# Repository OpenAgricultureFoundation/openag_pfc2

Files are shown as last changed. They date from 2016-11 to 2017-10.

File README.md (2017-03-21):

# openag_pfc2
This repository contains many resources for constructing a Personal Food Computer v2 (beta)

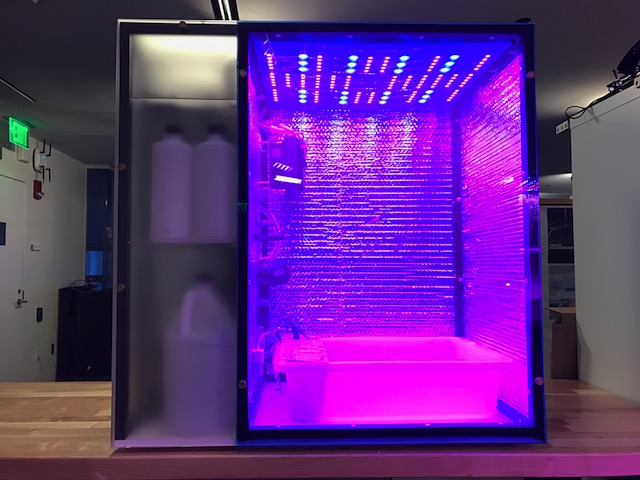
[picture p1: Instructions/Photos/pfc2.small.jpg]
pfc2


## Build Instructions

For many more photos and step by step build instructions, check out
[instructions.md](instructions.md).

## List of Resources

Resources included in this repository:
 - [Instructions](instructions.md): How to build a PFC2
 - [Build Video](https://youtu.be/Uf1FqjcPWsI): Video Walkthrough on the build. Good visual cues.
 - [Master Bill of Materials](BOM/BOM_MASTER.xlsx): Tabbed spreadsheet of components needed to
   build the PFC2
    - Ordering BOM: Components you will need to order from suppliers
    - Kit BOM: Components included in the PFC2 kit **\[NOTE: The kits are not available yet\]**
    - WIR-HAR-PCK-\*: Wiring harness component pack details
    - __FAS-PCK-0001: Fastener component pack details__ (The sheet with baggie number information on it)
    - STR-FOM-PCK-0001: Sealing foam component pack details
    - STR-PNL-PCK-\*: Panel and sticker component pack details
    - STR-BAR-PCK-0001: Bar component pack details
    - Raw Materials: Stock materials including aluminum bar, acrylic and HDPE panels,
      insulation, foam, etc. that can be used to make many of the components in the
      STR-BAR-\*, STR-PNL-\*, STR-FOM-\*, and STR-INS-\* component packs
 - [Sub Assembly Bill of Materials](BOM/BOM_Sub_Assemblys.xlsx): Tabbed spreadsheet of
   details on the sub assembly components
    - Temperature Control Assembly: Heating element, fan, and PC water cooling radiator
    - Chiller Assembly: Fan, mounting plate, and PC water cooling chiller
    - Peristaltic Pumps: Nutrient and pH solution pumps and pump mounting panel
    - Power Module: Power entry module, power switch, and DC power supplies
    - Light Manifold: LEDs, camera, and mounting panel
    - Water Manifold: Sensors, panels, pump, filter, etc.
    - Brain Manifold: Signal board, Raspberry Pi Model 3, Arduino Mega, etc.
 - [Solidworks CAD Model](CAD/GrabCAD/OpenAG-Personal-Food-Computer-V2): Comprehensive view of where
   parts belong in the computer
 - [Drawings](CAD/GrabCAD/Drawings): Documentation for machining parts or
   sending to a contract machinist
 - [DXF Files](CAD/GrabCAD/DXF): File format used for laser cutting parts
 - [Wire Harnesses](Wire_Harnesses.xlsx): Bill of Materials and instructions for creating
   the wire harnesses
 - [Wiring Reference](Wiring_Reference.xlsx): Reference when wiring up the device
 - [Connectorization](Connectorization.xlsx): Bill of Materials and instructions for
   attaching connectors to the chiller, fans, pumps, LEDs, etc.

### Tools
For 3D model Access, Go to [http://www.edrawingsviewer.com/](http://www.edrawingsviewer.com/) for a free & legitmate CAD document viewing software.

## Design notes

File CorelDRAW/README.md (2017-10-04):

# CorelDRAW files
These files were made by importing the .DXF files into CorelDRAW.
They are used on the Spirit laser cutter in the MIT ML Fab shop.

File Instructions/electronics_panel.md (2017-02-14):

## Assemble The Electronics Panel Components

#### Tools
- 1/16" Hex Driver
- 3/32" Hex Driver
- 1/4" Nut Driver
- 1/4" wrench

### Wire Seals
1. Gather foam squares **STR-FOM-0001**, **STR-FOM-0002**, & acrylic square **STR-PNL-0010**  from the foam pack.
2. Remove the adhesive protection from the foam
3. Match the patterns of the foam to their respective spots, and stick on.  **STR-FOM-0002** sticks to the electronics panel **STR-PNL-0017**, **STR-FOM-0001** sticks to the **STR-PNL-0010** backing plate.
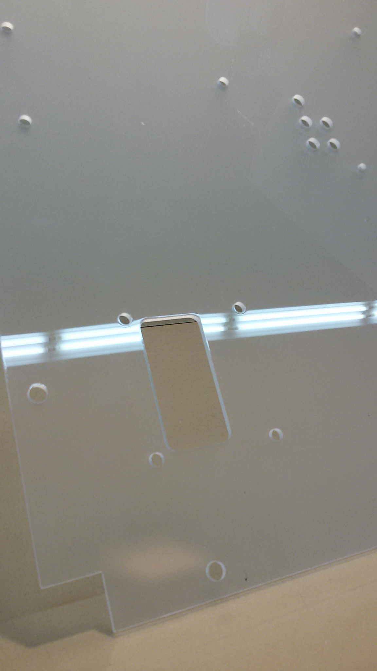
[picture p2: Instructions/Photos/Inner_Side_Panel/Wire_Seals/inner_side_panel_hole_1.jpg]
inner side panel hole

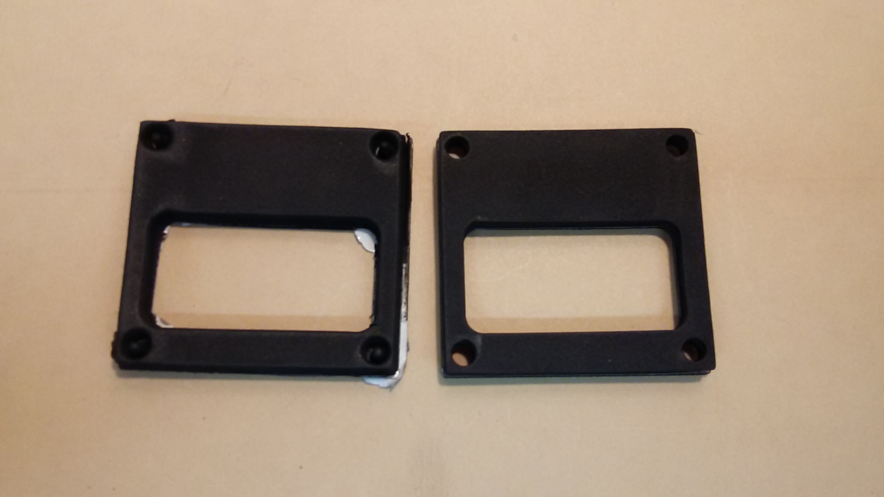
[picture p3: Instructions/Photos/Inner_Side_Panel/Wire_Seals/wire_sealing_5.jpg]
foam

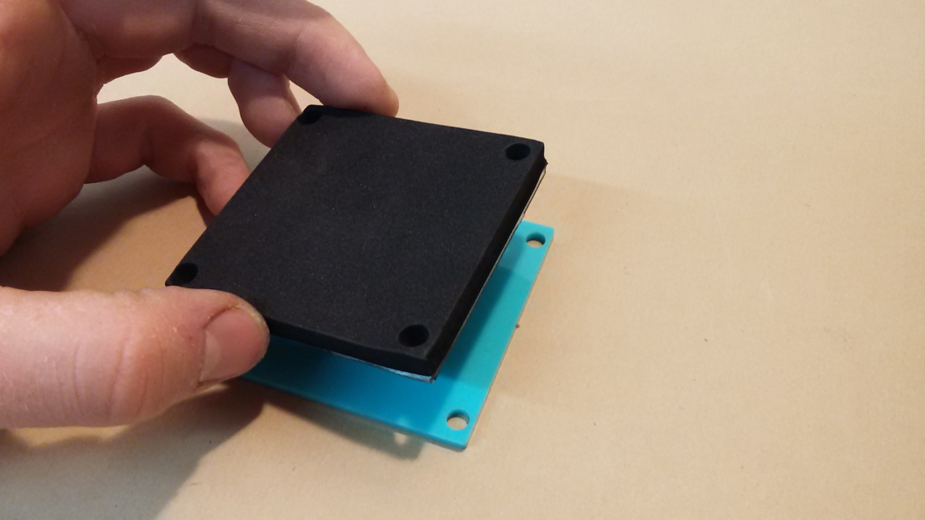
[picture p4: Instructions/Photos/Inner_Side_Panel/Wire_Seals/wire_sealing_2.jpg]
backing plate


4. Note the orientation arrow on the acrylic plate. This indicates the direction the wires should pass through to seal.

### Pump Assembly
1. Collect components listed in **Sub Assembly BOM's** **Peristaltic Pumps** tab.
2. Locate orientation arrow. The pumps mount relative to this.
3. Slot the pump through the hole, with attention to the direction its wires point.
4. All pumps wires should face to the right relative to the arrow. The tubes should face outward.
  * if the wires face the wrong direction, the body can be easily uncliped & rotated 90^o
5. Tighten each pump on using x2 **S-#04-40-375-BTN-S-SS (Bag 14)** (4-40 x 0375 button head) and **S-#04-40-094-NUT-H-SS (Bag 15)** (#4-40 nut)
6. Mount x4 **S-#08-32-250-STD-H-AL-FF (Bag 9)**(8-32x2.5 female alum standoff) in the remaining holes using **S-#08-32-375-BTN-S-SS (Bag 2)**(8-32x0375 button head)
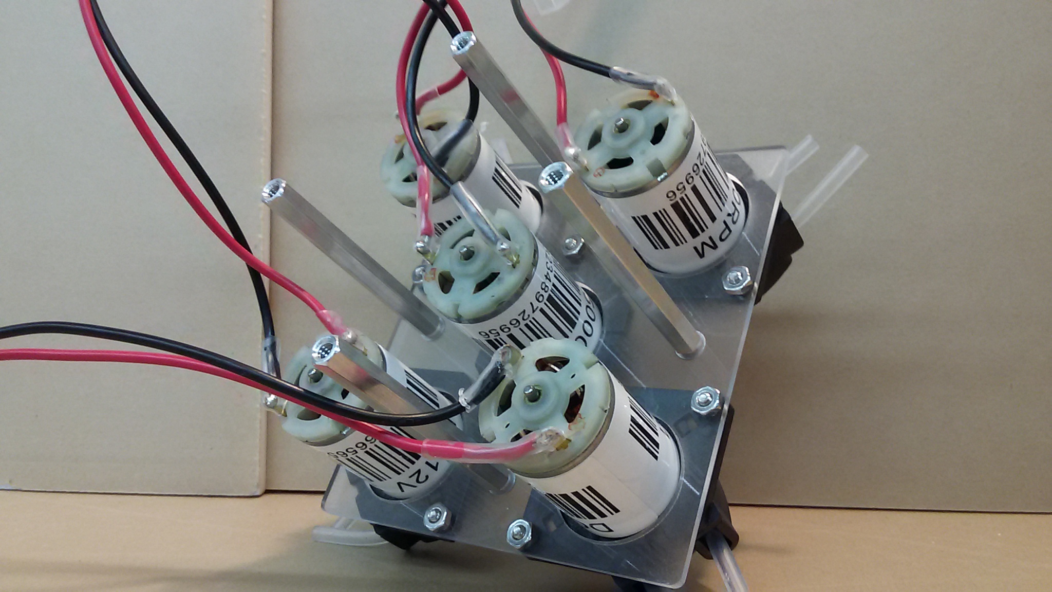
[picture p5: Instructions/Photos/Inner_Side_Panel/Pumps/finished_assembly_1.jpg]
Peristaltic Pumps Finished Assembly


### Side Camera
1. Stick adhesive backed **STR-FOM-0003 (Foam for camera sealing)** to the the camera **SEN-PRB-0005** board as shown.
2. Place the camera **SEN-PRB-0005** in its port on the inner side panel **STR-PNL-0017**, securing inplace with x4 **S-#02-56-375-BTN-S-SS (Bag 22)** & **S-#02-56-063-NUT-H-SS (Bag 23)**.  Note the orientationof the camera.
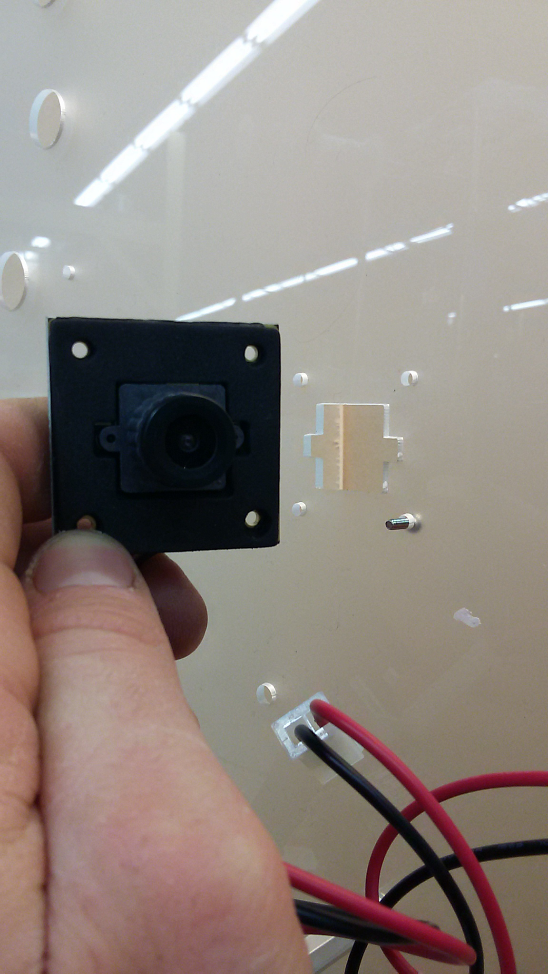
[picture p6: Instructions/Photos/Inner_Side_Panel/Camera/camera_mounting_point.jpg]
Camera with foam, at mounting point


### Humidity sensor
1. Place the Mount for the Humidity/temp sensor **SEN-MNT-0001** over its port. Secure inplace using x2 **S-#04-40-050-BTN-S-SS (Bag 11)** & **S-#04-40-094-NUT-H-SS (Bag 15)**.
2. Place the humidity sensor **SEN-PRB-CZD-0002** in at any time, tightening the screw on the side to secure the sensor.

### CO2 Sensor
1. Remove the CO2 sensor **SEN-PRB-CZD-0001** from its package, and put the small wire harness with black connectors to the side. This is not used.
2. Connect the harness with white connectors from the sensor to the blue board.
3. Push the sensor throught the port beneath the humidity/temp sensor port.
4. The small blue board can be neatly taped to the top of the sensor.
5. After full model assembly is complete, seal around its diameter with silicone sealant.
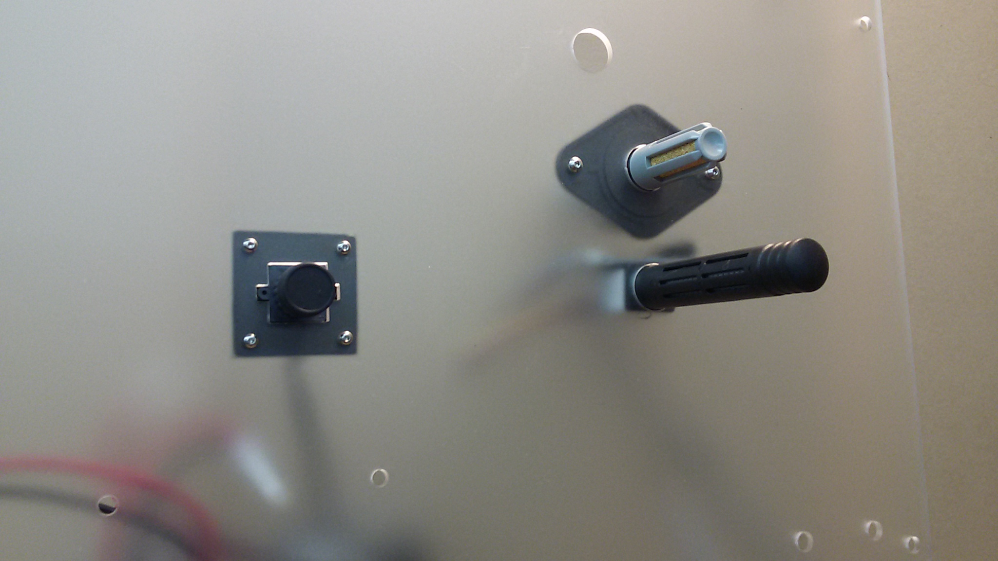
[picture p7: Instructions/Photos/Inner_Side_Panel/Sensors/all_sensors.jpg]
Picture of all sensors


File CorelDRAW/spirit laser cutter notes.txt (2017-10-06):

When corel prompts you to login, just hit "Skip" in the lower left.

Print > properties > paper tab - 960mm x 610mm   use this for page size.
You MUST check the Extend box.

When printing, use hairline pen type.  Select all, show object properties menu, select pen type hairline.

print then properties page for black color:
speed: 1.0
power: 100%
PPI: 1500
Air: on

For blue (if anything needs to be etched in the surface):
speed: 50.
power: 15%
PPI: default (400)
Air: on

You may need to print it a second time if it doesn't cut all the way through.

Anything you want etched, make blue then use lower power / higher speed.

Files:
- EB-panel-side is the left side cover for the electronics and side of fluid bay.
- EB-panel-front is the front fluid bay cover.
- door is the entrance to the growth chamber.

When using file "door with PFC etch", the black pen will do the lasing.  Set to 50/50/400

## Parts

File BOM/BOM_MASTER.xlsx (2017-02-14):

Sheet: Ordering BOM
Qty | Part Number | Description | Link | Distributor | Distributor Part Number
1 | STR-RAW-0010 | FOAM PLANT RAFT | https://www.amazon.com/Beaver-Plastics-Lettuce-Raft-72/dp/B01GG96JSA | Amazon
1 | ACT-CIR-0001 | NE555 Pulse Generator Adjustable Frequency Module 5-12V DC | https://www.amazon.com/gp/product/B00LHBZCCC/ref=oh_aui_search_detailpage?ie=UTF8&psc=1 | Amazon
1 | ACT-COV-0001 | 120mm Fan Guard | https://www.amazon.com/Metal-Finger-Guard-Computer-Cooling/dp/B00Y20QI0K | Amazon
1 | ACT-FLT-0001 | 1/2" Twist-On Pipe Strainer filter | https://www.amazon.com/gp/product/B000V2W0GE/ref=oh_aui_detailpage_o04_s00?ie=UTF8&psc=1 | Amazon
6 | ACT-FTG-0001 | G1/4" to 0375" Barb Fitting Black Chrome | https://www.amazon.com/s?url=search-alias%3Dcomputers&field-keywords=g1%2F4+to+3%2F8 | Amazon
1 | ACT-MIS-0001 | ASCS Small Active Aqua Air Stone Cylinder | https://www.amazon.com/gp/product/B00564Q784/ref=oh_aui_detailpage_o08_s00?ie=UTF8&psc=1 | Amazon
1 | ACT-PMP-0001 | Submersible Water Circulation Pump, 2.1 GPM | https://www.amazon.com/gp/product/B0196WL55G/ref=oh_aui_detailpage_o04_s00?ie=UTF8&psc=1 | Amazon
5 | ACT-PMP-0002 | Peristaltic Pump | https://www.amazon.com/Homecube-Peristaltic-Miniature-Aquarium-Analytical/dp/B0196LDFJQ | Amazon
1 | ACT-PMP-0003 | XSPC Ion Pump/reservoir combo | https://www.amazon.com/gp/product/B01BA3LY64/ref=oh_aui_detailpage_o04_s01?ie=UTF8&psc=1 | Amazon
1 | ACT-PMP-0004 | Mini Air Pump 12v Kpm27h Keurig Coffee Air Purge Pump | https://www.amazon.com/gp/product/B00ECCPT80/ref=oh_aui_detailpage_o01_s02?ie=UTF8&psc=1 | Amazon
40 | ACT-TBG-0001 | ATP Vinyl-Flex PVC Food Grade Plastic Tubing, Clear, 1/8" ID x 1/4" OD (By the Foot) | https://www.amazon.com/gp/product/B00E6BCV0G/ref=ox_sc_act_title_3?ie=UTF8&psc=1&smid=ATVPDKIKX0DER | Amazon
5 | ACT-TBG-0002 | PrimoFlex Advanced LRT 0375in.ID x 5/8in.OD Tubing Bundle (By the Foot) | https://www.amazon.com/gp/product/B00A0Q55MC/ref=ox_sc_act_title_2?ie=UTF8&psc=1&smid=A15YNZR7YB053N | Amazon
15 | ACT-TBG-0003 | Standard Airline Tubing (By the Inch) | https://www.amazon.com/gp/product/B0002APXOQ/ref=oh_aui_detailpage_o01_s01?ie=UTF8&psc=1 | Amazon
2 | ACT-VLV-0001 | 1/2" DC12V SS304 Motorized Valve,Electrical Ball Valve CR-02 | https://www.amazon.com/dp/B00OUTP6D8 | Amazon
1 | ACT-XNG-0001 | EX120 Single Fan Radiator | https://www.amazon.com/gp/product/B0067LW8HY/ref=oh_aui_detailpage_o00_s00?ie=UTF8&psc=1 | Amazon
1 | CSB-LIQ-0001 | General Hydroponics pH Up Liquid Fertilizer, 1-Quart | https://www.amazon.com/General-Hydroponics-Liquid-Fertilizer-1-Quart/dp/B005H78ZLC | Amazon
1 | CSB-LIQ-0002 | General Hydroponics pH Down Liquid Fertilizer, 1-Quart | https://www.amazon.com/General-Hydroponics-Liquid-Fertilizer-1-Quart/dp/B00CJID1I4 | Amazon
1 | CSB-LIQ-0003 | General Hydroponics FloraDuo A Mineral Nutrient, 1 Quart | https://www.amazon.com/General-Hydroponics-FloraDuo-Mineral-Nutrient/dp/B004PPY750 | Amazon
1 | CSB-LIQ-0004 | General Hydroponics FloraDuo B Mineral Nutrient, 1 Quart | https://www.amazon.com/General-Hydroponics-FloraDuo-Mineral-Nutrient/dp/B004IAB2F0 | Amazon
1 | CSB-MED-0001 | Oasis Horticubes (By the Tray of 104 Horticubes) | https://www.amazon.com/Oasis-Horticubes-2-Pack/dp/B007QVA7BS | Amazon
1 | ELC-MEM-0001 | SanDisk Ultra 32 GB Micro SDHC UHS-I | https://www.amazon.com/SanDisk-microSDHC-Standard-Packaging-SDSQUNC-032G-GN6MA/dp/B010Q57T02?s=pc | Amazon
1 | ELC-PRC-0001 | Arduino Mega 2560 w/USB A-to-B Cable | https://www.amazon.com/OSOYOO-MEGA2560-Control-ATMEGA2560-16AU-Compatible/dp/B00PD92EJ8?s=pc | Amazon
1 | ELC-PRC-0002 | Raspberry Pi 3 Model B | https://www.amazon.com/Raspberry-Pi-RASP-PI-3-Model-Motherboard/dp/B01CD5VC92?s=pc | Amazon
1 | ELC-REL-0001 | 16-Channel Relay Board | https://www.amazon.com/gp/product/B0057OC66U/ref=crt_ewc_title_dp_2?ie=UTF8&psc=1&smid=ATVPDKIKX0DER | Amazon
1 | ELC-REL-0002 | Multifunction Programmable Relay Timer | https://www.amazon.com/gp/product/B00VR1F3LC/ref=oh_aui_detailpage_o02_s02?ie=UTF8&psc=1 | Amazon
1 | FAS-MIS-0001 | 4" Mini Cable Ties, Black, (By the Pack of 100 Pieces) |  | Amazon
1 | PWR-REG-0001 | DC-DC Step-down Regulator 8-50V to 5V 3A with Micro USB Adapter Connector, Waterproof | https://www.amazon.com/gp/product/B00KKI4C1U/ref=ox_sc_act_title_4?ie=UTF8&psc=1&smid=AFHAE9RJVUMB | Amazon
1 | SEN-PRB-0003 | AM2315 Temperature & Humidity Sensor with Mount | https://www.amazon.com/gp/product/B011PR0WCW/ref=oh_aui_detailpage_o07_s01?ie=UTF8&psc=1 | Amazon
2 | SEN-PRB-0005 | ELP 2.1mm Wide Angle Mjpeg 5megapixel Hd Camera USB for Industrial,camera Module Usb Machine Vision | https://www.amazon.com/ELP-Camera-5megapixel-Industrial-Machine/dp/B00KA83C8O?s=electronics | Amazon
1 | STR-RAW-0007 | Reflectix, 24"x10' | https://www.amazon.com/REFLECTIX-BP24010-x10-Foil-Insulation/dp/B000BPF22U | Amazon
1 | STR-RAW-0013 | 1/8" adhesive backed neoprene foam, 39"x9" | https://www.amazon.com/Primode-sponge-Neoprene-Adhesive-Purpose/dp/B018DDM698 | Amazon
1 | STR-RAW-0014 | 1/4" adhesive backed neoprene foam, 39"x9" | https://www.amazon.com/Primode-sponge-Neoprene-Adhesive-Purpose/dp/B018DDM68Y | Amazon
1 | STR-SEA-0001 | Clear Food Grade Silicone Sealant - 2.8 oz Squeeze Tube | https://www.amazon.com/Silicone-Grade-Strength-Sealant-Clear/dp/B01F9HCDCQ | Amazon
1 | WIR-CBL-0012 | Inline Barrel Plug with Leads | https://www.amazon.com/Sinddy-Quality-10pack-5-5mm-Pigtail/dp/B00ZOFM2KC | Amazon
1 | WIR-CBL-0013 | 20 Pin 20 Way F/F Connector Rainbow Wire IDC Flat Ribbon Cable 48cm | https://www.amazon.com/dp/B00XP57W62 | Amazon
18 | WIR-SLD-0001 | 0.6mm Lead Free Solder (By the Inch) | https://www.amazon.com/Mudder-0-6mm-Ag0-3-0-22lb-Solder/dp/B01B61TWGY | Amazon
24 | WIR-TUB-0001 | Labellable Heat Shrink Tubing, 0.23" (By the Inch) | https://www.amazon.com/Anycolor-Compatible-Brother-HSE-211-HSE-611/dp/B01FETJD3G | Amazon
24 | WIR-TUB-0003 | 6mm Heat Shrink Tubing, Black (By the Inch) | https://www.amazon.com/uxcell-Meters-Shrink-Tubing-Shrinkable/dp/B008ASXLSC | Amazon
1 | SEN-CIR-0001 | EZO Conductivity Circuit | http://www.atlas-scientific.com/product_pages/circuits/ezo_ec.html | Atlas Scientific
1 | SEN-CIR-0002 | EZO pH Circuit | https://www.atlas-scientific.com/product_pages/circuits/ezo_ph.html | Atlas Scientific
1 | SEN-PRB-0002 | Atlas Conductivity Probe K 1.0 | http://www.atlas-scientific.com/product_pages/probes/ec_k1-0.html | Atlas Scientific
1 | SEN-PRB-0004 | Atlas pH Probe | https://www.atlas-scientific.com/product_pages/probes/ph_probe.html | Atlas Scientific
1 | SEN-SOL-0001 | Atlas EC Calibration Solution | http://www.atlas-scientific.com/product_pages/chemicals/ec-1_0.html | Atlas Scientific
1 | SEN-SOL-0002 | Atlas pH 4 Calibration 8 oz | https://www.atlas-scientific.com/product_pages/chemicals/ph4.html | Atlas Scientific
1 | SEN-SOL-0003 | Atlas pH 7 Calibration 8 oz | https://www.atlas-scientific.com/product_pages/chemicals/ph7.html | Atlas Scientific
1 | SEN-SOL-0004 | Atlas pH 10 Calibration 8 oz | https://www.atlas-scientific.com/product_pages/chemicals/ph10.html | Atlas Scientific
100 | S-018-32-075-PST-F-AL | Binder Post | http://www.bindingdepot.com/Shop-BD/Silver-Aluminum-Screw-Posts_2/3-4-in-Aluminum-Chicago-Screws-Screw-Posts-Qty-100-sets.html | Binding Depot
4 | M-004-00-022-FUT-O-RB | Rubber washer feet: BS-17 | http://www.bumperspecialties.com/index.php?main_page=product_info&cPath=6&products_id=64 | Bumper Specialties
1 | ELC-PCB-0001 | OpenAg Signal Board v1.0 | See Github | Choice of Fab House
4 | STR-RAW-0002 | Chemcast GP 2308 Turquoise Acrylic 0.125" Thick, 24"x48" | http://www.delviesplastics.com/p/Translucent_Cast_Acrylic_Sheet.html | Delvie's Plastics
1 | STR-RAW-0003 | 2069 transparent light blue Acrylic, 0.125" Thick, 24"x48"x0.125" | http://www.delviesplastics.com/p/Transparent_Acrylic.html | Delvie's Plastics
5 | STR-RAW-0004 | Frosted clear Acrylic, 0.125" Thick, 24"x48" | http://www.delviesplastics.com/p/Frosted-Acrylic-Sheet.html | Delvie's Plastics
1 | STR-RAW-0005 | Frosted clear Acrylic, 0.25" Thick, 12"x12" | http://www.delviesplastics.com/p/Frosted-Acrylic-Sheet.html | Delvie's Plastics
1 | ACT-FAN-0002 | AFB1212SHE Axial Fan 120x38mm, 152 CFM | https://www.digikey.com/product-detail/en/delta-electronics/AFB1212SHE/603-1082-ND/1014413 | Digikey
1 | ACT-FAN-0003 | CFM-A238-13-10 Axial Fan, 120x38mm, 201 CFM | https://www.digikey.com/product-detail/en/cui-inc/CFM-A238-13-10/102-4027-ND/6194935 | Digikey
2 | ELC-FUS-0001 | FUSE GLASS 10A 250VAC 5X20MM | http://www.digikey.com/product-detail/en/bel-fuse-inc/5SF-10-R/507-1235-ND/1009007 | Digikey
1 | ELC-PEM-0001 | Power Entry Module IEC 320-C14 Panel Mount, Snap-In, Fused | https://www.digikey.com/product-detail/en/qualtek/723W-X2-04/Q206-ND/245547 | Digikey
1 | ELC-RES-0001 | 4.7K Resistor 1/4W 5% Carbon Film | https://www.digikey.com/product-detail/en/stackpole-electronics-inc/CF14JT4K70/CF14JT4K70CT-ND/1830366 | Digikey
1 | ELC-SWI-0001 | Rocker Switch DPDT 20A (AC) 277V Panel Mount, Snap-In | https://www.digikey.com/product-detail/en/bulgin/C6060ALBB-1197W-B/1091-1204-ND/3459508 | Digikey
4 | PWR-BUS-0001 | 8-Pos Barrier Block | http://www.digikey.com/product-detail/en/molex-llc/0387700108/WM5765-ND/362492 | Digikey
4 | PWR-BUS-0002 | 8-Pos Barrier Block Jumper | http://www.digikey.com/product-detail/en/molex-llc/0380021290/WM5017-ND/604531 | Digikey
9 | WIR-CBL-0005 | 4-Con Multiconductor Cable, 24 AWG (By the Inch) | https://www.digikey.com/product-detail/en/general-cable-carol-brand/C2463A.41.10/C2463A-100-ND/5461325 | Digikey
52 | WIR-CBL-0006 | 3-Con Multiconductor Cable, 24 AWG (By the Inch) | https://www.digikey.com/product-detail/en/general-cable-carol-brand/C4062A.12.10/W121-100-ND/10726 | Digikey
1 | WIR-CBL-0010 | 7.5' Power Cord Black NEMA 5-15P To IEC 320-C13 (North American) | http://www.digikey.com/product-detail/en/qualtek/212013-01/Q124-ND/245573 | Digikey
26 | WIR-CON-0001 | 8 Stud Spade Terminal Connector Crimp 14-16 AWG | https://www.digikey.com/product-detail/en/molex-llc/0191440020/WM18356-ND/279157 | Digikey
6 | WIR-CON-0002 | 0.250" Quick Connect Terminal, Female, 10-12 AWG | https://www.digikey.com/product-detail/en/molex-llc/0196060002/WM2980-ND/2405558 | Digikey
2 | WIR-CON-0003 | 0.250" Quick Connect, Female, 14-16 AWG | https://www.digikey.com/product-detail/en/molex-llc/0190030040/WM18239-ND/279040 | Digikey
1 | WIR-CON-0004 | 0.250" Quick Connect, Female, 24-26 AWG | https://www.digikey.com/product-detail/en/molex-llc/0190030071/WM18235-ND/279036 | Digikey
48 | WIR-CTC-0001 | Molex Mini Fit Jr Contact, Pin, 16 AWG | https://www.digikey.com/product-detail/en/molex-llc/0039000082/WM1016-ND/1118559 | Digikey
48 | WIR-CTC-0002 | Molex Mini Fir Jr Contact, Socket, 16 AWG | https://www.digikey.com/product-detail/en/molex-llc/0039000077/WM3112CT-ND/1643460 | Digikey
6 | WIR-CTC-0005 | Molex SL Contact Crimp Pin 24-30 AWG | https://www.digikey.com/product-detail/en/molex-llc/0016020108/WM2565-ND/171962 | Digikey
21 | WIR-CTC-0006 | Molex SL Contact Crimp Socket 24-30 AWG | https://www.digikey.com/product-detail/en/molex-llc/0016020096/WM2562-ND/115060 | Digikey
21 | WIR-HOU-0001 | Molex Mini Fit Jr 2-Pos Plug | https://www.digikey.com/product-detail/en/molex-llc/0039013023/WM1030-ND/447277 | Digikey
21 | WIR-HOU-0002 | Molex Mini Fit Jr 2-Pos Recepticle | https://www.digikey.com/product-detail/en/molex-llc/0039013022/WM1021-ND/1118564 | Digikey
2 | WIR-HOU-0003 | Molex Mini Fit Jr 3-Pos Plug | http://www.digikey.com/product-detail/en/molex-llc/0039014036/WM18439-ND/300072 | Digikey
2 | WIR-HOU-0004 | Molex Mini Fit Jr 3-Pos Recepticle | http://www.digikey.com/product-detail/en/molex-llc/0039014030/WM18434-ND/300067 | Digikey
2 | WIR-HOU-0005 | Molex SL 4-Pos Rectangular Housing Connector Recepticle w/Latch, 0.100" | https://www.digikey.com/product-detail/en/molex-llc/0050579404/WM2902-ND/115057 | Digikey
7 | WIR-HOU-0006 | Molex SL 4-Pos Rectangular Housing Connector Plug w/Latch, 0.100" | https://www.digikey.com/product-detail/en/molex-llc/0701070003/WM2535-ND/210970 | Digikey
8 | STR-CON-0001 | 3/4" 3-Way Esto Connector, Black | http://www.estoconnectors.com/product/pn-533075 | Esto Connectors | 533075-BX
5 | STR-CON-0002 | 3/4" 4-Way Special Esto Connector, Black | http://www.estoconnectors.com/product/pn-5457sp1 | Esto Connectors | 5457SP-BX
3 | STR-CON-0003 | 3/4" Right Angle Esto Connector, Black | http://www.estoconnectors.com/product/pn-521075 | Esto Connectors | 521075-BX
6 | STR-RAW-0001 | 0.75" Square aluminum frame tube, 8ft length, 0.75in square | http://www.estoconnectors.com/product/pn-160726 | Esto Connectors | 160726-AB
21 | S-025-20-075-RVT-O-S | Rivet Nut | https://www.fastenal.com/products/details/41680 | Fastenal | 41680
1 | ACT-LGT-0001 | GrowMAX Red LED, 24 Modules, 12" Lead | Coming Soon! | GE
1 | ACT-LGT-0002 | TetraMAX White LED, 10 Modules, 12" Lead | Coming Soon! | GE
1 | ACT-LGT-0003 | GrowMAX Blue LED, 8 Modules, 12" Lead | Coming Soon! | GE
1 | STR-RAW-0008 | MDF Board, 0.5" thick, 24"x48 | http://www.homedepot.com/p/1-2-in-x-2-ft-x-4ft-Medium-Density-Fiberboard-1508108/202089097 | Home Depot
2 | ACT-FTG-0002 | Brass Barbed Hose Elbow, 90 Degree Angle, 0375" Hose ID, 1/2 NPT Male End | https://www.mcmaster.com/#53525k57/=15snqb0 | Mcmaster | 53525K57
6 | FST-RIV-0001 | Rivet, Aluminum, Domed, 3/16" Diameter | https://www.mcmaster.com/#97447a050/=15spibg | McMaster | 97447A050
10 | M-004-07-005-BTN-S-SS | m4x5mm button head | https://www.mcmaster.com/#92095a477/=15spi6u | McMaster | 92095A477
2 | M-004-07-014-BTN-S-SS | M4 x 14mm button head | https://www.mcmaster.com/#92095a193/=15spi3b | McMaster | 92095A193
4 | S-#02-56-018-STD-H-SS-FF | (2-56 x 0.1875 female female ss standoff) | https://www.mcmaster.com/#91780a006/=15w9jgg | McMaster | 91780A006
8 | S-#02-56-025-BTN-S-SS | 2-56 x 1/4 button head | https://www.mcmaster.com/#92949a077/=15spixx | McMaster | 92949A077
4 | S-#02-56-050-STD-H-AL-FF | 2-56 x 1/2 female female aluminum standoff | https://www.mcmaster.com/#91115a107/=15spj07 | McMaster | 91115A107
4 | S-#02-56-063-NUT-H-SS | #2-56 nuts | https://www.mcmaster.com/#catalog/122/3200/=15spipi | McMaster | 91841A003
4 | S-#02-56-375-BTN-S-SS | #2-56 x 0375 button head Screw | https://www.mcmaster.com/#catalog/122/3128/=15spitq | McMaster | 92949A079
24 | S-#04-40-025-BTN-S-SS | 4-40 x 1/4 button head | https://www.mcmaster.com/#92949a106/=15spijv | McMaster | 92949A106
8 | S-#04-40-025-STD-H-AL-MF | 4-40 x 1/4 body alum standoff Female-3/16 length male | https://www.mcmaster.com/#93505a101/=15spiuw | McMaster | 93505A101
8 | S-#04-40-025-STD-H-NY-FF | 4-40 x 1/4 standoff, nylon | https://www.mcmaster.com/#92319a865/=15spixf | McMaster | 92319A865
22 | S-#04-40-050-BTN-S-SS | #4-40 1/2 button head | https://www.mcmaster.com/#92949a110/=15spieu | McMaster | 92949A110
4 | S-#04-40-075-STD-H-AL-FF | 4-40 x 3/4 aluminum standoff Female Femal | https://www.mcmaster.com/#91780a535/=15spirc | McMaster | 91780A535
34 | S-#04-40-094-NUT-H-SS | #4-40 nut | https://www.mcmaster.com/#91841a005/=15spioh | McMaster | 91841A005
8 | S-#04-40-125-BTN-S-SS | 4-40 x 1/8 button head | https://www.mcmaster.com/#92949a103/=15spiho | McMaster | 92949A103
4 | S-#04-40-125-STD-H-AL-FF | 4-40 alum female femal standoff | https://www.mcmaster.com/#91780a034/=15spj2z | McMaster | 91780A034
12 | S-#04-40-375-BTN-S-SS | 4-40 x 0375 button head | https://www.mcmaster.com/#92949a108/=15spim1 | McMaster | 92949A108
2 | S-#06-32-312-BTN-S-SS | 6-32 x 5/16 button head | https://www.mcmaster.com/#92196a145/=15spib8 | McMaster | 92196A145
3 | S-#08-00-045-WSH-O-S | Zinc-Plated Steel Washer, #08 Screw Size | https://www.mcmaster.com/#94744a224/=15spgcc | McMaster | 94744A224
12 | S-#08-00-125-LBR-O-S | (L bracket zinc plated steel) | https://www.mcmaster.com/#1556a26/=15w9i54 | McMaster | 1556A26
5 | S-#08-00-125-LBR-O-SS | L bracket | https://www.mcmaster.com/#1556a65/=15sphu2 | McMaster | 1556A65
3 | S-#08-00-875-SPC-O-AL | 1/4 OD x 7/8 L alum Spacer | https://www.mcmaster.com/#92510a468/=15sphge | McMaster | 92510A468
4 | S-#08-32-025-BTN-S-SS | 8-32 x 1/4 button head | https://www.mcmaster.com/#92949a190/=15spfuh | McMaster | 92949A190
13 | S-#08-32-050-BTN-S-SS | 8-32 x 1/2 button head | https://www.mcmaster.com/#92949a194/=15spg4g | McMaster | 92949A194
27 | S-#08-32-075-BTN-S-SS | #8-32 x 3/4 button head | https://www.mcmaster.com/#92949a197/=15sphnc | McMaster | 92949A197
100 | S-#08-32-094-NUT-H-SS | 8-32 Nut | https://www.mcmaster.com/#90730a009/=15sphw3 | McMaster | 90730A009
3 | S-#08-32-100-BTN-S-SS | (8-32 x1.25 L SS button head) | https://www.mcmaster.com/#92949a199/=15w9ino | MCMaster | 92949A199
8 | S-#08-32-100-STD-H-AL-FF | 8-32 x 1 standoff, aluminum | https://www.mcmaster.com/#91780a198/=15spi0g | McMaster | 91780A198
8 | S-#08-32-125-BTN-S-SS | (8-32 x1.25 L SS button head) | https://www.mcmaster.com/#92949a201/=15w9izz | MCMaster | 92949A201
3 | S-#08-32-150-BTN-S-SS | (8-32 x1.5 L SS button head) | https://www.mcmaster.com/#92949a203/=15w9j6w | McMaster | 92949A203
4 | S-#08-32-150-STD-H-AL-FF | 8-32 x 1.5 female standoff | https://www.mcmaster.com/#91780a202/=15spi46 | McMaster | 91780A202
6 | S-#08-32-175-BTN-S-SS | 8-32 x 1.75 button head partially threaded | https://www.mcmaster.com/#92949a205/=15sphr4 | McMaster | 92949A205
4 | S-#08-32-250-STD-H-AL-FF | 8-32x2.5 female alum standoff | https://www.mcmaster.com/#91780a047/=15spi7e | McMaster | 91780A047
41 | S-#08-32-375-BTN-S-SS | 8-32 x 0375 button head | https://www.mcmaster.com/#92949a192/=15spg04 | McMaster | 92949A192
5 | S-#08-32-375-FUT-O-S | chiller plate feet | https://www.mcmaster.com/#9541k2/=15sphl0 | McMaster | 9541K2
4 | S-#10-00-075-SPC-O-AL | 0375 OD x 3/4 L alum spacer | https://www.mcmaster.com/#92510a647/=15sphyr | McMaster | 92510A647
7 | S-025-20-075-THB-O-BR | Knurled head 1/4-20 thumb screw | https://www.mcmaster.com/#92421a540/=15spimz | McMaster | 92421A540
1 | S-025-20-100-UBL-O-SS | Ubolt, 1/4 20 thread. For Ball Valve | https://www.mcmaster.com/#8896t119/=15sphp8 | McMaster | 8896T119
14 | S-025-20-438-BTN-S-SS | 1/4-20 x 7/16 screw | https://www.mcmaster.com/#92949a833/=15spifk | McMaster | 92949A833
2 | S-050-NN-019-NUT-O-PL | 1/2 NPT Plastic locknut | https://www.mcmaster.com/#7945k81/=15spgu7 | McMaster | 7945K81
6 | STR-CLP-0001 | Hose Clamp, 17/32" to 39/64" ID | https://www.mcmaster.com/#53175k88/=15sn2mt | McMaster | 53175K88
1 | STR-FOM-0004 | Adhesive-Back Strip, Coarse, 1/4" Thick, 3/4" Width (By the 50' Roll) | https://www.mcmaster.com/#93745k43/=15oj36u | McMaster | 93745K43
1 | STR-RAW-0006 | Hdpe plastic, 12"x24"x0.0625" | https://www.mcmaster.com/#8619k422/=15s8aob | McMaster
1 | STR-RAW-0009 | Aluminum Sheetmetal, 1/16" thick (14 gauge), 18"x18"x0.0625" | https://www.mcmaster.com/#89015k189/=15saoey | McMaster
1 | SEN-PRB-0007 | DS18B20 Waterproof Temperature Sensor | http://www.newegg.com/Product/Product.aspx?Item=9SIA7BF2K18425 | Newegg
606 | WIR-CBL-0001 | Stranded Hookup Wire (300V), 16 AWG, Black (By the Inch) | https://powerwerx.com/stranded-hookup-wire-300volt-ul1007 | Powerwerx | Wire-ST-16-00-100
679 | WIR-CBL-0002 | Stranded Hookup Wire (300V), 16 AWG, Red (By the Inch) | https://powerwerx.com/stranded-hookup-wire-300volt-ul1007 | Powerwerx | Wire-ST-16-02-100
36 | WIR-CBL-0003 | Stranded Hookup Wire (300V), 16 AWG, White (By the Inch) | https://powerwerx.com/stranded-hookup-wire-300volt-ul1007 | Powerwerx | Wire-ST-16-09-100
40 | WIR-CBL-0004 | Stranded Hookup Wire (300V), 16 AWG, Green (By the Inch) | https://powerwerx.com/stranded-hookup-wire-300volt-ul1007 | Powerwerx | Wire-ST-16-05-100
26 | WIR-CBL-0007 | Stranded Hookup Wire (300V), 24 AWG, Red (By the Inch) | https://powerwerx.com/stranded-hookup-wire-300volt-ul1007 | Powerwerx | Wire-ST-24-02-100
37 | WIR-CBL-0008 | Stranded Hookup Wire (300V), 24 AWG, White (By the Inch) | https://powerwerx.com/stranded-hookup-wire-300volt-ul1007 | Powerwerx | Wire-ST-24-09-100
44 | WIR-CBL-0009 | Stranded Hookup Wire (300V), 24 AWG, Yellow (By the Inch) | https://powerwerx.com/stranded-hookup-wire-300volt-ul1007 | Powerwerx | Wire-ST-24-04-100
4 | WIR-CBL-0015 | Stranded Hookup Wire (300V), 24 AWG, Black (By the Inch) | https://powerwerx.com/stranded-hookup-wire-300volt-ul1007 | Powerwerx | Wire-ST-24-00-100
1 | SEN-PRB-0001 | MHZ16 CO2 Sensor, 10000ppm | http://sandboxelectronics.com/ | Sandbox Electronics
1 | STR-RAW-0011 | White Vinyl, 12"x10yds | https://www.signwarehouse.com/c/12-x-10-yds-72320 | Sign Warehouse
1 | STR-RAW-0012 | Orange Vinyl, 12"x10yds | https://www.signwarehouse.com/c/12-x-10-yds-72320 | Sign Warehouse
2 | ACT-FAN-0001 | Squirrel Cage Blower, 16 CFM | https://www.sparkfun.com/products/11270 | Sparkfun
2 | SEN-PRB-0006 | LLE102000 Liquid Level Sensor | https://www.sparkfun.com/products/13835 | Sparkfun
1 | PWR-SUP-0001 | RSP-320-24 24VDC 320W Switching Power Supply | https://www.trcelectronics.com/View/Mean-Well/RSP-320-24.shtml | TRC Electronics
1 | PWR-SUP-0002 | SE-45012 12VDC 450W Power Supply | https://www.trcelectronics.com/View/Mean-Well/SE-450-12.shtml | TRC Electronics
1 | STR-RSV-0002 | 1 Gallon Round Jug with 38/400 Cap | http://www.usplastic.com/catalog/item.aspx?itemid=26054 | U.S. Plastic Corp
1 | ACT-HTR-0001 | 12V 300W PTC Heating Element | https://www.walmart.com/ip/12V-300W-PTC-Heating-Element-Heater-Plate-with-Black-Metal-Hoder/120677364?wmlspartner=wlpa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 | Walmart
1 | STR-RSV-0001 | Rubbermaid 3349-92 20" x 15" x 5" White Plastic Bus Box | http://www.webstaurantstore.com/rubbermaid-3349-92-20-x-15-x-5-white-plastic-bus-box-fg334992wht/702334992WH.html | Webstaurantstore
5 | ACT-MIS-0002 | Size No. 7 Black Rubber Stopper, 2 Hole | http://www.widgetco.com/7-2-hole-rubber-stoppers-plugs | Widgetco

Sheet: Kit BOM
Qty | Part Number | Description
1 | ACT-CHL-0001 | KippKitt's Chiller Compressor
1 | ACT-CIR-0001 | NE555 Pulse Generator Adjustable Frequency Module 5-12V DC
1 | ACT-CIR-0002 | Compressor Driver Board
1 | ACT-COV-0001 | 120mm Fan Guard
1 | ACT-FAN-CZD-0002 | AFB1212SHE Axial Fan 120x38mm, 152 CFM, Connectorized
1 | ACT-FAN-CZD-0003 | CFM-A238-13-10 Axial Fan, 120x38mm, 201 CFM, Connectorized
1 | ACT-FLT-0001 | 1/2" Twist-On Pipe Strainer filter
6 | ACT-FTG-0001 | G1/4" to 0375" Barb Fitting Black Chrome
2 | ACT-FTG-0002 | 90 Degree Angle, 0375" Hose ID, 1/2 NPT Male End
1 | ACT-HTR-CZD-0001 | 12V 300W PTC Heating Element, Connectorized
1 | ACT-LGT-CZD-0001 | GrowMAX Red LED, 24 Modules, 12" Lead, Connectorized
1 | ACT-LGT-CZD-0002 | TetraMAX White LED, 10 Modules, 12" Lead, Connectorized
1 | ACT-LGT-CZD-0003 | GrowMAX Blue LED, 8 Modules, 12" Lead, Connectorized
1 | ACT-MIS-0001 | ASCS Small Active Aqua Air Stone Cylinder
5 | ACT-MIS-0002 | Size No. 7 Black Rubber Stopper, 2 Hole
2 | ACT-MIS-CZD-0001 | Squirrel Cage Blower, 16 CFM and 050 DC12V SS304 Motorized Valve,Electrical Ball Valve CR-02, Connectorized
1 | ACT-PMP-CZD-0001 | Submersible Water Circulation Pump, 2.1 GPM with LED Light, Connectorized
5 | ACT-PMP-CZD-0002 | Peristaltic Pump, Connectorized
1 | ACT-PMP-CZD-0003 | Ion Reservoir/Pump Combo, Connectorized
1 | ACT-PMP-CZD-0004 | Mini Air Pump, Connectorized
40 | ACT-TBG-0001 | ATP Vinyl-Flex PVC Food Grade Plastic Tubing, Clear, 1/8" ID x 1/4" OD (By the Foot)
5 | ACT-TBG-0002 | PrimoFlex Advanced LRT 0375in.ID x 5/8in.OD Tubing Bundle (By the Foot)
15 | ACT-TBG-0003 | Standard Airline Tubing (By the Inch)
1 | ACT-XNG-0001 | EX120 Single Fan Radiator
1 | CSB-LIQ-0001 | General Hydroponics pH Up Liquid Fertilizer, 1-Quart
1 | CSB-LIQ-0002 | General Hydroponics pH Down Liquid Fertilizer, 1-Quart
1 | CSB-LIQ-0003 | General Hydroponics FloraDuo A Mineral Nutrient, 1 Quart
1 | CSB-LIQ-0004 | General Hydroponics FloraDuo B Mineral Nutrient, 1 Quart
1 | CSB-MED-0001 | Oasis Horticubes (By the Tray of 104 Horticubes)
2 | ELC-FUS-0001 | FUSE GLASS 10A 250VAC 5X20MM
1 | ELC-MEM-0001 | SanDisk Ultra 32 GB Micro SDHC UHS-I
1 | ELC-PCB-0001 | OpenAg Signal Board v1.0
1 | ELC-PEM-0001 | Power Entry Module IEC 320-C14 Panel Mount, Snap-In, Fused
1 | ELC-PRC-0001 | Arduino Mega 2560 w/USB A-to-B Cable
1 | ELC-PRC-0002 | Raspberry Pi 3 Model B
1 | ELC-REL-0001 | 16-Channel Relay Board
1 | ELC-REL-0002 | Multifunction Programmable Relay Timer
1 | ELC-SWI-0001 | Rocker Switch DPDT 20A (AC) 277V Panel Mount, Snap-In
1 | FAS-MIS-0001 | 4" Mini Cable Ties, Black, (By the Pack of 100 Pieces)
1 | FAS-PCK-0001 | Assortment of Fasteners and Joiners for PFC2 Kit, Version 1
4 | PWR-BUS-0001 | 8-Pos Barrier Block
4 | PWR-BUS-0002 | 8-Pos Barrier Block Jumper
1 | PWR-REG-CZD-0001 | DC-DC Step-down Regulator 8-50V to 5V 3A with Micro USB Adapter Connector, Waterproof, Connectorized
1 | PWR-SUP-0001 | RSP-320-24 24VDC Switching Power Supply
1 | PWR-SUP-0002 | SE-45012 12VDC Power Supply
1 | SEN-CIR-0001 | EZO Conductivity Circuit
1 | SEN-CIR-0002 | EZO pH Circuit
1 | SEN-MNT-0001 | AM2315 Temperature & Humidity Sensor Mount
1 | SEN-PRB-0001 | MHZ16 CO2 Sensor, 10000ppm
1 | SEN-PRB-CZD-0001 | MHZ16 CO2 Sensor, 10000ppm, Connectorized
1 | SEN-PRB-0002 | Atlas Conductivity Probe K 1.0
1 | SEN-PRB-0004 | Atlas pH Probe
2 | SEN-PRB-0005 | ELP 2.1mm Wide Angle Mjpeg 5megapixel Hd Camera USB for Industrial,camera Module Usb Machine Vision
1 | SEN-PRB-CZD-0002 | AM2315 Temperature & Humidity Sensor, Connectorized
1 | SEN-PRB-CZD-0003 | DS18B20 Waterproof Temperature Sensor, Connectorized
2 | SEN-PRB-CZD-0004 | LLE102000 Liquid Level Sensor, Connectorized
4 | STR-BAR-PCK-0001 | Aluminum Frame Bar Package, Includes STR-BAR-0001 to STR-BAR-0010
6 | STR-CLP-0001 | Hose Clamp, 17/32" to 39/64" ID
8 | STR-CON-0001 | 3/4" 3-Way Esto Connector, Black
5 | STR-CON-0002 | 3/4" 4-Way Special Esto Connector, Black
3 | STR-CON-0003 | 3/4" Right Angle Esto Connector, Black
1 | STR-FOM-0004 | Adhesive-Back Strip, Coarse, 1/4" Thick, 3/4" Width (By the 50' Roll)
1 | STR-FOM-PCK-0001 | Foam for Wire Pass-Thrus and Camera. Includes STR-FOM-0001 to STR-FOM-0003
1 | STR-INS-0001 | outer-top-plate insulation
1 | STR-INS-0002 | Outer side panel insulation
1 | STR-INS-0003 | Rearsheet insulation
1 | STR-INS-0004 | inner-side-panel insulation
1 | STR-PNL-0001 | Baseplate
1 | STR-PNL-0002 | Power Supply Bracket
2 | STR-PNL-0003 | Power Supply Bracket small
1 | STR-PNL-0031 | Raft with 7 Square Holes, 13.5" x 15.5" x 1"
1 | STR-PNL-PCK-0001 | Vinyl Sticker Package, Includes STR-PNL-0027 to STR-PNL-0030
1 | STR-PNL-PCK-0002 | Acrylic Panel Package, Includes STR-PNL-004 to STR-PNL-0026
1 | STR-RSV-0001 | Rubbermaid 3349-92 20" x 15" x 5" White Plastic Bus Box
1 | STR-RSV-0002 | 1 Gallon Round Jug with Cap
1 | STR-SEA-0001 | Clear Food Grade Silicone Sealant - 2.8 oz Squeeze Tube
1 | WIR-CBL-0010 | 7.5' Power Cord Black NEMA 5-15P To IEC 320-C13 (North American)
1 | WIR-CBL-0013 | 20 Pin 20 Way F/F Connector Rainbow Wire IDC Flat Ribbon Cable 48cm
1 | WIR-CBL-CZD-0001 | Inline Barrel Plug with Leads, Connectorized
1 | WIR-HAR-PCK-0001 | Wire Harnesses for Brain Manifold Sub-assembly, Version 1
1 | WIR-HAR-PCK-0002 | Wire Harnesses for Power Manifold Sub-assembly, Version 1
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

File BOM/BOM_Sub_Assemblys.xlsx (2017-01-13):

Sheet: Temperature Control Assembly
PART NUMBER | DESCRIPTION | QTY.
ACT-XNG-0001 EX120 Single Fan Radiator | EX120 Single Fan Radiator | 1
ACT-FTG-0001 G025 to 0375 Barb Fitting Black Chrome | G025 to 0375 Barb Fitting Black Chrome | 2
CFM-A238-13-10 Axial Fan | Axial Fan 120x38mm 201 CFM Connectorized | 1
ACT-HTR-CZD-0001 | 12V 300W PTC Heating Element, Connectorized | 1
S-#08-32-150-STD-H-AL-FF | (8-32 x 1.5 female standoff) | 4
S-#08-32-375-BTN-S-SS | (8-32x0375 button head) | 8
S-#06-32-312-BTN-S-SS | (6-32 x 03125 button head) | 2

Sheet: Chiller Assembly
ITEM NO. | PART NUMBER | DESCRIPTION | QTY.
1 | STR-PNL-0007 | Chiller Base Plate, Frosted Clear Acrylic | 1
2 | S-#08-32-375-FUT-O-S (chiller plate feet) | (chiller plate feet) | 5
3 | S-#08-00-125-LBR-O-SS L bracket stainless steel | Stainless steel L Bracket | 8
4 | CFM-A238-13-10 Axial Fan 120x38mm 201CFM Connectorized | Axial Fan 120x38mm 201CFM Connectorized | 1
5 | S-#08-32-094-NUT-H-SS (8-32 Nut) | (8-32 Nut) | 22
6 | ACT-PMP-CZD-0003 Ion Reservoir-Pump Combo Connectorized | Ion Reservoir-Pump Combo Connectorized | 1
7 | S-#08-32-375-BTN-S-SS (8-32x0375 button head) | (8-32x0375 button head) | 11
8 | S-#08-32-050-BTN-S-SS (8-32 x 050 button head) | (8-32 x 050 button head) | 2
9 | S-#08-00-875-SPC-O-AL (025 OD x 0875 L alum Spacer) | (025 OD x 0875 L alum Spacer) | 3
10 | S-#08-32-150-BTN-S-SS (8-32 x1.5 L SS button head) | S-#08-32-150-BTN-S-SS (8-32 x1.5 L SS button head) | 3

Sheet: Peristaltic Pumps
Peristalic pumps
ITEM NO. | PART NUMBER | DESCRIPTION | QTY.
1 | STR-PNL-0013 Pump Mounting panel Frosted Clear | Pump Mounting panel Frosted Clear | 1
2 | ACT-PMP-CZD-0002 Peristaltic Pump | Connectorized peristaltic pump | 5
3 | S-#08-32-250-STD-H-AL-FF (8-32x2.5 female alum standoff) | (8-32x2.5 female alum standoff) | 4
4 | S-#04-40-375-BTN-S-SS (4-40 x 0375 button head) | (4-40 x 0375 button head) | 10
5 | S-#08-32-375-BTN-S-SS (8-32x0375 button head) | (8-32x0375 button head) | 4
6 | S-#04-40-094-NUT-H-SS (#4-40 nut) | (#4-40 nut) | 10

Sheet: Power Module
Qty | Part Number (Description)
2 | ELC-FUS-0001 (FUSE GLASS 10A 250VAC 5X20MM)
1 | ELC-PEM-0001 (Power Entry Module)
1 | ELC-REL-0002 (Multifunction Programmable Relay Timer)
1 | ELC-SWI-0001 (Rocker Switch DPDT 20A (AC) 277V Panel Mount)
10 | M-004-07-005-BTN-S-SS (m4x5mm button head)
2 | M-004-07-014-BTN-S-SS (M4 x 14mm button head)
1 | PWR-SUP-0001 (RSP-320-24 24VDC Switching Power Supply)
1 | PWR-SUP-0002 (SE-45012 12VDC Power Supply)
4 | S-#04-40-025-BTN-S-SS (4-40 x 025 button head)
4 | S-#04-40-025-STD-H-AL-MF (4-40 x 025 body alum standoff Female-01875 length male)
4 | S-#04-40-094-NUT-H-SS (#4-40 nut)
4 | S-#08-32-025-BTN-S-SS (8-32 x 025 button head)
4 | S-#08-32-094-NUT-H-SS (8-32 Nut)
1 | STR-PNL-0002 (Power Supply Bracket)
2 | STR-PNL-0003 (Power Supply Bracket Small)
1 | WIR-HAR-PCK-0002 (Wire Harnesses for Power Manifold Sub-assembly, Version 1)

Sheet: Light Manifold
ITEM NO. | PART NUMBER | DESCRIPTION | QTY.
1 | STR-PNL-0006 | Light Panel Solid Turquoise | 1
2 | ACT-LGT-CZD-0001 | GrowMAX Red LED 24 Modules 12" Lead Connectorized | 24
3 | ACT-LGT-CZD-0002 | TetraMAX White LED 10 Modules 12" Lead Connectorized | 10
4 | ACT-LGT-CZD-0003 | GrowMAX Blue LED 8 Modules 12" Lead Connectorized | 8
5 | SEN-PRB-0005 | ELP 2mm Wide Angle Mjpeg 5megapixel Hd Camera USB for Industrial camera Module Usb Machine Vision | 1
6 | S-#02-56-018-STD-H-SS-FF | (2-56 x 0.1875 female female ss standoff) | 4
7 | S-#02-56-025-BTN-S-SS | (2-56 x 025 button head) | 8
8 | STR-PNL-0011 | Light Strap | 2
9 | STR-PNL-0012 | Light Strap | 2
10 | S-#08-32-075-BTN-S-SS | (#8-32 x 075 button head) | 16
11 | S-#08-32-094-NUT-H-SS | (8-32 Nut) | 16

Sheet: Water Manifold
ITEM NO. | PART NUMBER | DESCRIPTION | QTY.
1 | STR-PNL-0004 | Water Manifold Horizontal Panel HDPE | 1
2 | STR-PNL-0005 | Water Manifold Vertical HDPE | 1
3 | ACT-PMP-CZD-0001 | Submersible Water Circulation Pump, 2.1 GPM with LED Light, Connectorized | 1
4 | S-#08-00-125-LBR-O-SS L bracket stainless steel | Stainless steel L Bracket | 7
5 | SEN-PRB-0002 Atlas Conductivity Probe K 1 | AtlasConductivity Probe K 1 | 1
6 | SEN-PRB-0004 Atlas pH Probe | Atlas pH Probe | 1
7 | STR-PNL-0031 | Raft with 7 Square Holes 13 x 15 x 1 | 1
8 | SEN-PRB-CZD-0003 | DS18B20 Waterproof Temperature Sensor Connectorized | 1
9 | STR-PNL-0009 | Water Manifold Level Sensor Mounting Panel HDPE | 1
10 | S-#08-32-050-BTN-S-SS (8-32 x 050 button head) | (8-32 x 050 button head) | 1
11 | S-#08-32-094-NUT-H-SS (8-32 Nut) | (8-32 Nut) | 1
12 | ACT-FLT-0001 | 1/2" Twist-On Pipe Strainer filter | 1
13 | SEN-PRB-CZD-0004 | LLE102000 Liquid Level Sensor Connectorized | 2
14 | STR-PNL-0008 | Water Manifold Accessory Panel HDPE | 2
15 | S-050-NN-019-NUT-O-PL | (050 NPT Plastic locknut) | 2

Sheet: Brain Manifold
Qty | Part Number (Description)
1 | ELC-PCB-0001 (OpenAg Signal Board v1.0)
1 | ELC-PRC-0001 (Arduino Mega 2560 USB A-to-B Cable)
1 | ELC-PRC-0002 (Raspberry Pi 3 Model B)
1 | ELC-REL-0001 (16-Channel Relay Board)
1 | FAS-MIS-0001 (4" Mini Cable Ties, Black, 100 Piece Pack)
4 | PWR-BUS-0001 (8-Pos Barrier Block)
4 | PWR-BUS-0002 (8-Pos Barrier Block Jumper)
1 | PWR-REG-CZD-0001 (Step-down Regulator with Micro USB Plug, Connectorized)
16 | S-#04-40-025-BTN-S-SS (4-40 x 025 button head)
4 | S-#04-40-025-STD-H-AL-MF (4-40 x 025 body alum standoff Female-01875 length male)
8 | S-#04-40-025-STD-H-NY-FF (4-40 x 025 standoff nylon)
16 | S-#04-40-050-BTN-S-SS (#4-40 050 button head)
4 | S-#04-40-075-STD-H-AL-FF (4-40 x 0375aluminum standoff Female Female)
18 | S-#04-40-094-NUT-H-SS (#4-40 nut)
8 | S-#04-40-125-BTN-S-SS (4-40 x 0125 button head)
2 | S-#04-40-375-BTN-S-SS (4-40 x 0375 button head)
8 | S-#08-32-050-BTN-S-SS (8-32 x 050 button head)
8 | S-#08-32-100-STD-H-AL-FF (8-32 x 1 standoff)
1 | STR-PNL-0014 (Brain Manifold Panel Frosted Clear)
1 | STR-PNL-0015 (Raspberry Pi Mounting Panel, frosted clear)
1 | WIR-CBL-0013 (20 pos ribbon cable, female-to-female, 48cm)
1 | WIR-CBL-CZD-0001 (Inline Barrel Plug with Leads, Connectorized)
1 | WIR-HAR-PCK-0001 (Wire Harnesses for Brain Manifold Sub-assembly, Version 1)

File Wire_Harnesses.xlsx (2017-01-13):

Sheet: BOM
Qty | Part Number | Description
576 | WIR-CBL-0001 | Stranded Hookup Wire (300V), 16 AWG, Black (By the Inch)
651 | WIR-CBL-0002 | Stranded Hookup Wire (300V), 16 AWG, Red (By the Inch)
36 | WIR-CBL-0003 | Stranded Hookup Wire (300V), 16 AWG, White (By the Inch)
40 | WIR-CBL-0004 | Stranded Hookup Wire (300V), 16 AWG, Green (By the Inch)
46 | WIR-CBL-0006 | 3-Con Multiconductor Cable, 24 AWG (By the Inch)
26 | WIR-CBL-0007 | Stranded Hookup Wire (300V), 24 AWG, Red (By the Inch)
33 | WIR-CBL-0008 | Stranded Hookup Wire (300V), 24 AWG, White (By the Inch)
44 | WIR-CBL-0009 | Stranded Hookup Wire (300V), 24 AWG, Yellow (By the Inch)
22 | WIR-CON-0001 | 8 Stud Spade Terminal Connector Crimp 14-16 AWG
6 | WIR-CON-0002 | 0.250" Quick Connect Terminal, Female, 10-12 AWG
2 | WIR-CON-0003 | 0.250" Quick Connect, Female, 14-16 AWG
1 | WIR-CON-0004 | 0.250" Quick Connect, Female, 24-26 AWG
10 | WIR-CTC-0001 | Molex Mini Fit Jr Contact, Pin, 16 AWG
48 | WIR-CTC-0002 | Molex Mini Fir Jr Contact, Socket, 16 AWG
6 | WIR-CTC-0005 | Molex SL Contact Crimp Pin 24-30 AWG
17 | WIR-CTC-0006 | Molex SL Contact Crimp Socket 24-30 AWG
5 | WIR-HOU-0001 | Molex Mini Fit Jr 2-Pos Plug
21 | WIR-HOU-0002 | Molex Mini Fit Jr 2-Pos Recepticle
2 | WIR-HOU-0004 | Molex Mini Fit Jr 3-Pos Recepticle
2 | WIR-HOU-0005 | Molex SL 4-Pos Rectangular Housing Connector Recepticle w/Latch, 0.100"
3 | WIR-HOU-0006 | Molex SL 4-Pos Rectangular Housing Connector Plug w/Latch, 0.100"
3 | WIR-TUB-LBL-0001 | Labellable Heat Shrink Tubing, 0.23", Label "24V"
2 | WIR-TUB-LBL-0002 | Labellable Heat Shrink Tubing, 0.23", Label "12V@1"
2 | WIR-TUB-LBL-0003 | Labellable Heat Shrink Tubing, 0.23", Label "12V@2"
2 | WIR-TUB-LBL-0004 | Labellable Heat Shrink Tubing, 0.23", Label "12V@3"
1 | WIR-TUB-LBL-0005 | Labellable Heat Shrink Tubing, 0.23", Label "K1"
1 | WIR-TUB-LBL-0006 | Labellable Heat Shrink Tubing, 0.23", Label "K1-COM"
1 | WIR-TUB-LBL-0007 | Labellable Heat Shrink Tubing, 0.23", Label "K1-NO"
1 | WIR-TUB-LBL-0008 | Labellable Heat Shrink Tubing, 0.23", Label "K2"
1 | WIR-TUB-LBL-0009 | Labellable Heat Shrink Tubing, 0.23", Label "K3"
1 | WIR-TUB-LBL-0010 | Labellable Heat Shrink Tubing, 0.23", Label "K4"
1 | WIR-TUB-LBL-0011 | Labellable Heat Shrink Tubing, 0.23", Label "K5"
1 | WIR-TUB-LBL-0012 | Labellable Heat Shrink Tubing, 0.23", Label "K6"
1 | WIR-TUB-LBL-0013 | Labellable Heat Shrink Tubing, 0.23", Label "K7"
1 | WIR-TUB-LBL-0014 | Labellable Heat Shrink Tubing, 0.23", Label "K8@1"
1 | WIR-TUB-LBL-0015 | Labellable Heat Shrink Tubing, 0.23", Label "K8@2"
1 | WIR-TUB-LBL-0016 | Labellable Heat Shrink Tubing, 0.23", Label "K8-NC"
1 | WIR-TUB-LBL-0017 | Labellable Heat Shrink Tubing, 0.23", Label "K8-NO"
1 | WIR-TUB-LBL-0018 | Labellable Heat Shrink Tubing, 0.23", Label "K10"
1 | WIR-TUB-LBL-0019 | Labellable Heat Shrink Tubing, 0.23", Label "K11"
1 | WIR-TUB-LBL-0020 | Labellable Heat Shrink Tubing, 0.23", Label "K12"
1 | WIR-TUB-LBL-0021 | Labellable Heat Shrink Tubing, 0.23", Label "K13"
1 | WIR-TUB-LBL-0022 | Labellable Heat Shrink Tubing, 0.23", Label "K14"
1 | WIR-TUB-LBL-0023 | Labellable Heat Shrink Tubing, 0.23", Label "K15"
1 | WIR-TUB-LBL-0024 | Labellable Heat Shrink Tubing, 0.23", Label "K16"
2 | WIR-TUB-LBL-0025 | Labellable Heat Shrink Tubing, 0.23", Label "D3"
2 | WIR-TUB-LBL-0026 | Labellable Heat Shrink Tubing, 0.23", Label "D4"
1 | WIR-TUB-LBL-0027 | Labellable Heat Shrink Tubing, 0.23", Label "RPI GPIO 11/13/15/17"
2 | WIR-TUB-LBL-0028 | Labellable Heat Shrink Tubing, 0.23", Label "12V@4"
1 | WIR-TUB-LBL-0029 | Labellable Heat Shrink Tubing, 0.23", Label "K9"
1 | WIR-TUB-LBL-0030 | Labellable Heat Shrink Tubing, 0.23", Label "K9-COM"
1 | WIR-TUB-LBL-0031 | Labellable Heat Shrink Tubing, 0.23", Label "K9-NO"

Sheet: WIR-HAR-PCK-0001
Qty | Part Number | Description | End 1 Connector / Housing | End 1 Housing Position | End 1 Contact | End 1 Wire Heat Shrink Tubing / Label | End 1 Wire Tin? | End 1 Wire Strip Length (Inches) | Wire / Cable | Wire / Cable Length (Inches) | End 2 Wire Strip Length (Inches) | End 2 Wire Tin? | End 2 Wire Heat Shrink Tubing / Label | End 2 Contact | End 2 Housing Position | End 2 Connector / Housing
1 | WIR-HAR-0001 | 8 Stud 14-16 AWG Spade Terminal with 2" Red Wire Lead | - | - | - | - | y | 0.25 | WIR-CBL-0002 | 2 | 0.25 | - | - | - | - | WIR-CON-0001
1 | WIR-HAR-0002 | 8 Stud 14-16 AWG Spade Terminal with 2.5" Black Wire Lead | - | - | - | - | y | 0.25 | WIR-CBL-0001 | 2.5 | 0.25 | - | - | - | - | WIR-CON-0001
14 | WIR-HAR-0003 | 8 Stud 14-16 AWG Spade Terminal with 10" Red Wire Lead | - | - | - | - | y | 0.25 | WIR-CBL-0002 | 10 | 0.25 | - | - | - | - | WIR-CON-0001
1 | WIR-HAR-0004 | Molex JR 2-Pos Recepticle-to-Recepticle Cable with "24V" Label, 26" | WIR-HOU-0002 | 1 | WIR-CTC-0002 | - | - | 0.125 | WIR-CBL-0001 | 26 | 0.125 | - | - | WIR-CTC-0002 | 1 | WIR-HOU-0002
 |  |  |  | 2 | WIR-CTC-0002 | WIR-TUB-LBL-0001 | - | 0.125 | WIR-CBL-0002 | 26 | 0.125 | - | WIR-TUB-LBL-0001 | WIR-CTC-0002 | 2
1 | WIR-HAR-0005 | Molex JR 2-Pos Recepticle to 8 Stud 14-16 AWG Spade Terminals with "12V@1" Label, 10" Leads | WIR-HOU-0002 | 1 | WIR-CTC-0002 | - | - | 0.125 | WIR-CBL-0001 | 10 | 0.125 | - | - | - | - | WIR-CON-0001
 |  |  |  | 2 | WIR-CTC-0002 | WIR-TUB-LBL-0002 | - | 0.125 | WIR-CBL-0002 | 10 | 0.125 | - | - | - | - | WIR-CON-0001
1 | WIR-HAR-0006 | Molex JR 2-Pos Recepticle to 8 Stud 14-16 AWG Spade Terminals with "12V@2" Label, 10" Black Lead, 8" Red Lead | WIR-HOU-0002 | 1 | WIR-CTC-0002 | - | - | 0.125 | WIR-CBL-0001 | 10 | 0.125 | - | - | - | - | WIR-CON-0001
 |  |  |  | 2 | WIR-CTC-0002 | WIR-TUB-LBL-0003 | - | 0.125 | WIR-CBL-0002 | 8 | 0.125 | - | - | - | - | WIR-CON-0001
1 | WIR-HAR-0007 | Molex JR 2-Pos Recepticle-to-Recepticle with "12V@3" and "K1" Labels on 21" Red Leads with 15" Black Interconnect | WIR-HOU-0002 | 2 | WIR-CTC-0002 | WIR-TUB-LBL-0004 | - | 0.125 | WIR-CBL-0002 | 21 | 0.25 | y | WIR-TUB-LBL-0007 | - | - | -
 |  |  |  | 1 | WIR-CTC-0002 | - | - | 0.125 | WIR-CBL-0001 | 15 | 0.125 | - | - | WIR-CTC-0002 | 1 | WIR-HOU-0002
 |  |  | - | - | - | WIR-TUB-LBL-0006 | y | 0.25 | WIR-CBL-0002 | 21 | 0.125 | - | WIR-TUB-LBL-0005 | WIR-CTC-0002 | 2
1 | WIR-HAR-0008 | Molex JR 2-Pos Recepticle with "K2" Label to 21" Black Lead with 8 Stud 14-16 AWG Spade Terminals, 24" Red Lead | WIR-HOU-0002 | 1 | WIR-CTC-0002 | - | - | 0.125 | WIR-CBL-0001 | 21 | 0.25 | - | - | - | - | WIR-CON-0001
 |  |  |  | 2 | WIR-CTC-0002 | WIR-TUB-LBL-0008 | - | 0.125 | WIR-CBL-0002 | 24 | 0.25 | y | - | - | - | -
1 | WIR-HAR-0009 | Molex JR 2-Pos Recepticle with "K3" Label to 21" Black Lead with 8 Stud 14-16 AWG Spade Terminals, 24" Red Lead | WIR-HOU-0002 | 1 | WIR-CTC-0002 | - | - | 0.125 | WIR-CBL-0001 | 21 | 0.25 | - | - | - | - | WIR-CON-0001
 |  |  |  | 2 | WIR-CTC-0002 | WIR-TUB-LBL-0009 | - | 0.125 | WIR-CBL-0002 | 24 | 0.25 | y | - | - | - | -
1 | WIR-HAR-0010 | Molex JR 2-Pos Recepticle with "K4" Label to 21" Black Lead with 8 Stud 14-16 AWG Spade Terminals, 24" Red Lead | WIR-HOU-0002 | 1 | WIR-CTC-0002 | - | - | 0.125 | WIR-CBL-0001 | 21 | 0.25 | - | - | - | - | WIR-CON-0001
 |  |  |  | 2 | WIR-CTC-0002 | WIR-TUB-LBL-0010 | - | 0.125 | WIR-CBL-0002 | 24 | 0.25 | y | - | - | - | -
1 | WIR-HAR-0011 | Molex JR 2-Pos Recepticle with "K5" Label to 17" Black Lead with 8 Stud 14-16 AWG Spade Terminals, 18" Red Lead | WIR-HOU-0002 | 1 | WIR-CTC-0002 | - | - | 0.125 | WIR-CBL-0001 | 15 | 0.25 | - | - | - | - | WIR-CON-0001
 |  |  |  | 2 | WIR-CTC-0002 | WIR-TUB-LBL-0011 | - | 0.125 | WIR-CBL-0002 | 18 | 0.25 | y | - | - | - | -
1 | WIR-HAR-0012 | Molex JR 2-Pos Recepticle with "K6" Label to 36" Black Lead with 8 Stud 14-16 AWG Spade Terminals, 42" Red Lead | WIR-HOU-0002 | 1 | WIR-CTC-0002 | - | - | 0.125 | WIR-CBL-0001 | 36 | 0.25 | - | - | - | - | WIR-CON-0001
 |  |  |  | 2 | WIR-CTC-0002 | WIR-TUB-LBL-0012 | - | 0.125 | WIR-CBL-0002 | 42 | 0.25 | y | - | - | - | -
1 | WIR-HAR-0013 | Molex JR 2-Pos Recepticle with "K7" Label to 30" Black Lead with 8 Stud 14-16 AWG Spade Terminals, 36" Red Lead | WIR-HOU-0002 | 1 | WIR-CTC-0002 | - | - | 0.125 | WIR-CBL-0001 | 30 | 0.25 | - | - | - | - | WIR-CON-0001
 |  |  |  | 2 | WIR-CTC-0002 | WIR-TUB-LBL-0013 | - | 0.125 | WIR-CBL-0002 | 36 | 0.25 | y | - | - | - | -
1 | WIR-HAR-0014 | Molex JR 3-Pos Recepticles with "K8@1" and "K8@2" Labels, Spliced together with "K8-NC" and "K8-NO" labelled leads | WIR-HOU-0004 | 1 | WIR-CTC-0002 | - | - | 0.125 | WIR-CBL-0001 | 30 | 0.25 | - | - | - | - | WIR-CON-0001
 |  |  |  | 2 | WIR-CTC-0002 | - | - | 0.125 | WIR-CBL-0002 | 34 | 0.25 | - | - | - | - | Splice into 12" lead, pos 2, @end-3"
 |  |  |  | 3 | WIR-CTC-0002 | WIR-TUB-LBL-0014 | - | 0.125 | WIR-CBL-0002 | 34 | 0.25 | - | - | - | - | Splice into 12" lead, pos 2, @end-3"
 |  |  | WIR-HOU-0004 | 1 | WIR-CTC-0002 | - | - | 0.125 | WIR-CBL-0001 | 16 | 0.25 | - | - | - | - | WIR-CON-0001
 |  |  |  | 2 | WIR-CTC-0002 | - | - | 0.125 | WIR-CBL-0002 | 12 | 0.25@end, 0.25@end-3" | y | WIR-TUB-LBL-0016 | - | - | -
 |  |  |  | 3 | WIR-CTC-0002 | WIR-TUB-LBL-0015 | - | 0.125 | WIR-CBL-0002 | 12 | 0.25@end, 0.25@end-3" | y | WIR-TUB-LBL-0017 | - | - | -
1 | WIR-HAR-0015 | Molex JR 2-Pos Recepticle with "K10" Label to 22" Black Lead with 8 Stud 14-16 AWG Spade Terminals, 29" Red Lead | WIR-HOU-0002 | 1 | WIR-CTC-0002 | - | - | 0.125 | WIR-CBL-0001 | 22 | 0.25 | - | - | - | - | WIR-CON-0001
 |  |  |  | 2 | WIR-CTC-0002 | WIR-TUB-LBL-0018 | - | 0.125 | WIR-CBL-0002 | 29 | 0.25 | y | - | - | - | -
1 | WIR-HAR-0016 | Molex JR 2-Pos Recepticle with "K11" Label to 22" Black Lead with 8 Stud 14-16 AWG Spade Terminals, 29" Red Lead | WIR-HOU-0002 | 1 | WIR-CTC-0002 | - | - | 0.125 | WIR-CBL-0001 | 22 | 0.25 | - | - | - | - | WIR-CON-0001
 |  |  |  | 2 | WIR-CTC-0002 | WIR-TUB-LBL-0019 | - | 0.125 | WIR-CBL-0002 | 29 | 0.25 | y | - | - | - | -
1 | WIR-HAR-0017 | Molex JR 2-Pos Recepticle with "K12" Label to 19" Black Lead with 8 Stud 14-16 AWG Spade Terminals, 27" Red Lead | WIR-HOU-0002 | 1 | WIR-CTC-0002 | - | - | 0.125 | WIR-CBL-0001 | 19 | 0.25 | - | - | - | - | WIR-CON-0001
 |  |  |  | 2 | WIR-CTC-0002 | WIR-TUB-LBL-0020 | - | 0.125 | WIR-CBL-0002 | 27 | 0.25 | y | - | - | - | -
1 | WIR-HAR-0018 | Molex JR 2-Pos Recepticle with "K13" Label to 19" Black Lead with 8 Stud 14-16 AWG Spade Terminals, 27" Red Lead | WIR-HOU-0002 | 1 | WIR-CTC-0002 | - | - | 0.125 | WIR-CBL-0001 | 19 | 0.25 | - | - | - | - | WIR-CON-0001
 |  |  |  | 2 | WIR-CTC-0002 | WIR-TUB-LBL-0021 | - | 0.125 | WIR-CBL-0002 | 27 | 0.25 | y | - | - | - | -
1 | WIR-HAR-0019 | Molex JR 2-Pos Recepticle with "K14" Label to 19" Black Lead with 8 Stud 14-16 AWG Spade Terminals, 27" Red Lead | WIR-HOU-0002 | 1 | WIR-CTC-0002 | - | - | 0.125 | WIR-CBL-0001 | 19 | 0.25 | - | - | - | - | WIR-CON-0001
 |  |  |  | 2 | WIR-CTC-0002 | WIR-TUB-LBL-0022 | - | 0.125 | WIR-CBL-0002 | 27 | 0.25 | y | - | - | - | -
1 | WIR-HAR-0020 | Molex JR 2-Pos Recepticle with "K15" Label to 19" Black Lead with 8 Stud 14-16 AWG Spade Terminals, 27" Red Lead | WIR-HOU-0002 | 1 | WIR-CTC-0002 | - | - | 0.125 | WIR-CBL-0001 | 19 | 0.25 | - | - | - | - | WIR-CON-0001
 |  |  |  | 2 | WIR-CTC-0002 | WIR-TUB-LBL-0023 | - | 0.125 | WIR-CBL-0002 | 27 | 0.25 | y | - | - | - | -
1 | WIR-HAR-0021 | Molex JR 2-Pos Recepticle with "K16" Label to 19" Black Lead with 8 Stud 14-16 AWG Spade Terminals, 27" Red Lead | WIR-HOU-0002 | 1 | WIR-CTC-0002 | - | - | 0.125 | WIR-CBL-0001 | 19 | 0.25 | - | - | - | - | WIR-CON-0001
 |  |  |  | 2 | WIR-CTC-0002 | WIR-TUB-LBL-0024 | - | 0.125 | WIR-CBL-0002 | 27 | 0.25 | y | - | - | - | -
1 | WIR-HAR-0022 | Molex SR 4-Pos Recepticle-to-Plug with "D3" Labels, 26" | WIR-HOU-0005 | 1 | WIR-CTC-0005 | - | - | 0.125 | WIR-CBL-0006 (BLK) | 26 | 0.125 | - | - | WIR-CTC-0006 | 1 | WIR-HOU-0006
 |  |  |  | 2 | WIR-CTC-0005 | WIR-TUB-LBL-0025 | - | 0.125 | WIR-CBL-0006 (RED) |  | 0.125 | - | WIR-TUB-LBL-0025 | WIR-CTC-0006 | 2
 |  |  |  | 3 | WIR-CTC-0005 | - | - | 0.125 | WIR-CBL-0006 (GRN) |  | 0.125 | - | - | WIR-CTC-0006 | 3
 |  |  |  | 4 | - | - | - | - | - |  | - | - | - | - | 4
1 | WIR-HAR-0023 | Molex SR 4-Pos Recepticle-to-Plug with "D4" Labels, 26" | WIR-HOU-0005 | 1 | WIR-CTC-0005 | - | - | 0.125 | WIR-CBL-0006 (BLK) | 26 | 0.125 | - | - | WIR-CTC-0006 | 1 | WIR-HOU-0006
 |  |  |  | 2 | WIR-CTC-0005 | WIR-TUB-LBL-0026 | - | 0.125 | WIR-CBL-0006 (RED) |  | 0.125 | - | WIR-TUB-LBL-0026 | WIR-CTC-0006 | 2
 |  |  |  | 3 | WIR-CTC-0005 | - | - | 0.125 | WIR-CBL-0006 (GRN) |  | 0.125 | - | - | WIR-CTC-0006 | 3
 |  |  |  | 4 | - | - | - | - | - |  | - | - | - | - | 4
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

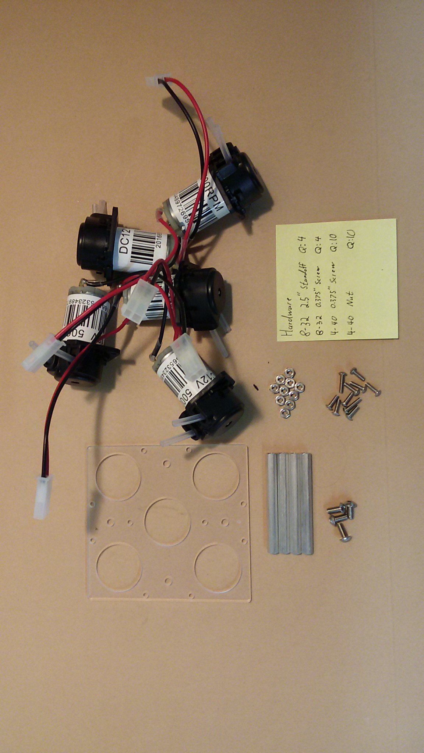
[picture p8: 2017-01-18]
Instructions/Photos/Inner_Side_Panel/Pumps/all_components.jpg

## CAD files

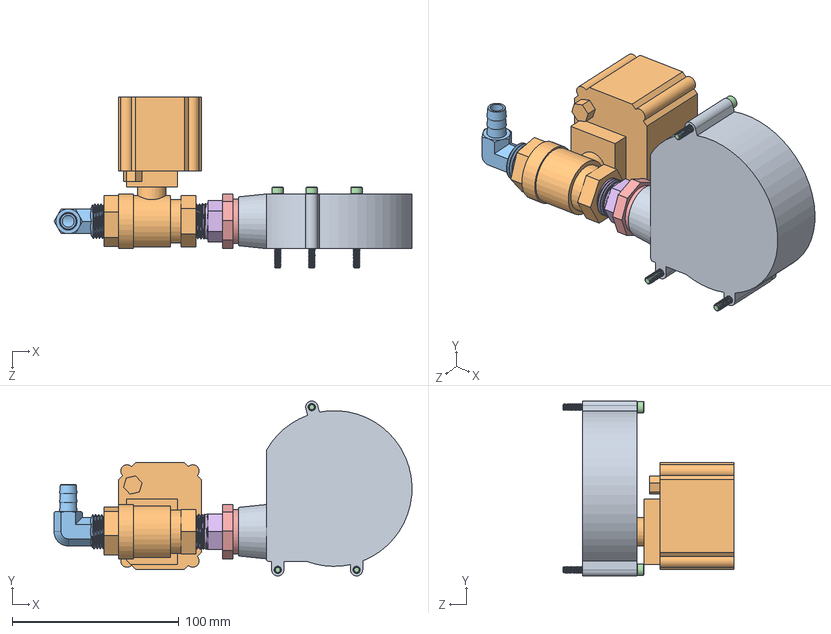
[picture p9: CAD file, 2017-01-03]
CAD/GrabCAD/OpenAG-Personal-Food-Computer-V2/Air Flush/Air Flush In.SLDASM
214.5 x 104.8 x 102.6 mm
blower_fan
ball_valve
050NPT to 375ID 90 degBRASS BARBED HOSE FITTING
8-32_screw 1.75 x 3
PVC pipe bushing 3_4 male to 1_2 femal
1_2 NPT pvc pipe adapter

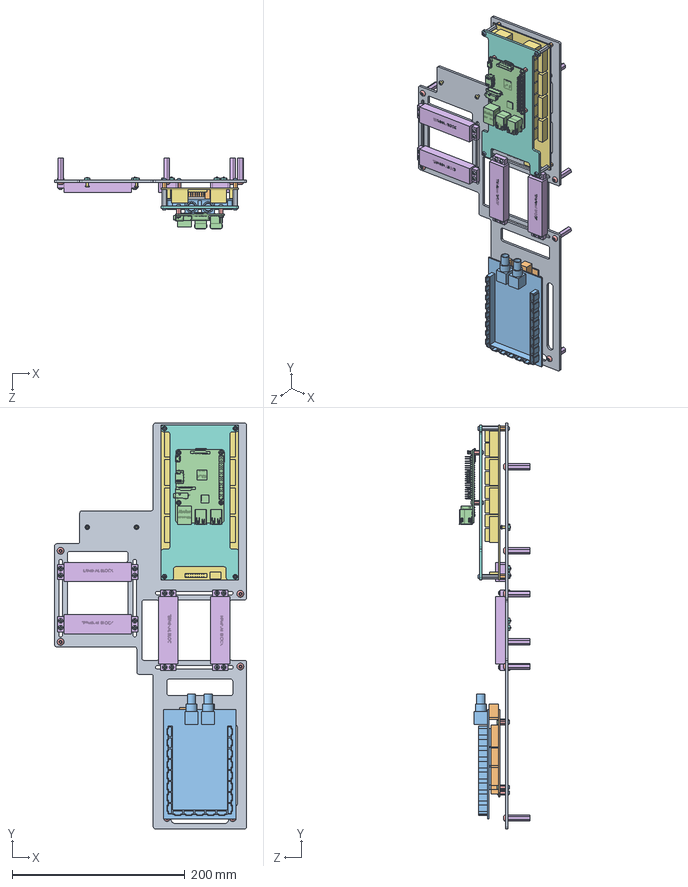
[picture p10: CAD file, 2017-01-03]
CAD/GrabCAD/OpenAG-Personal-Food-Computer-V2/brain_manifold/brain_manifold_assembly.SLDASM
222.2 x 469.9 x 82.0 mm
brain_manifold
Arduino Mega R3
signal-board
raspberry-pi-B+
standoff-4-40-f-f-nylon x 8
S-008-100-STD-O-AL-001_8-32_standoff_f-f_p25hex x 8
sainsmart-16-relay
pi-mount-2
S-004-075-STD-O-AL-001_4-40-FF-standoff-AL-p75L-p187hex x 4
S-004-025-STD-O-AL-002_4-40-MF-standoff-AL-p25L x 4
S-004-025-BTN-H-SS-001-440x1_4-button-head-screw x 16
S-004-012-BTN-H-SS-001-440x1_8-button-head-screw x 8
S-008-050-BTN-H-SS-001-832x1_2-button-head-screw x 8
Molex Terminal Block x 4
S-004-038-BTN-H-SS-001-440x3_8-button-head-screw x 2
S-004-NUT-SS-001-440-SS-Nut-3_8thk x 18
S-004-050-BTN-H-SS-001-440x1_2-button-head-screw x 16

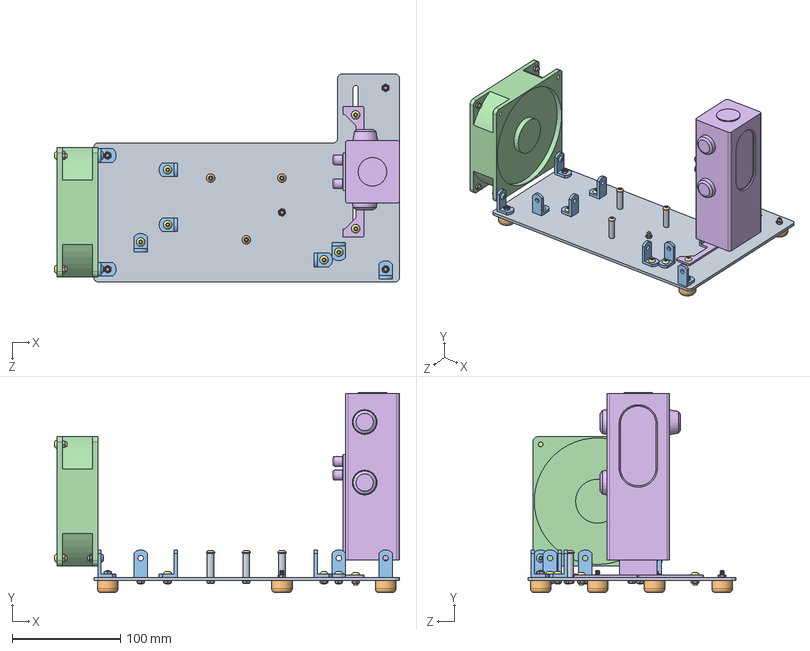
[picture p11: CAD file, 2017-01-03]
CAD/GrabCAD/OpenAG-Personal-Food-Computer-V2/Chiller/Chiller Compartment/Chiller Plate.SLDASM
318.4 x 185.0 x 191.8 mm
Chiller base plate
RUBBER_BUMPER WITH 8-32x375 THREADED STUD x 5
l-bracket_correct x 8
120mm_fan
S-008-NUT-SS-001_832-SS-Nut-3-32thk x 22
Pump_Reservoir
S-008-038-BTN-H-SS-001-832x3_8-button-head-screw x 11
S-008-050-BTN-H-SS-001-832x1_2-button-head-screw x 2
008 875ALUM UNTHRD SPACER x 3
S-008-1125-STD-O-AL-001_832xp1125_standoff_p1125hex x 3

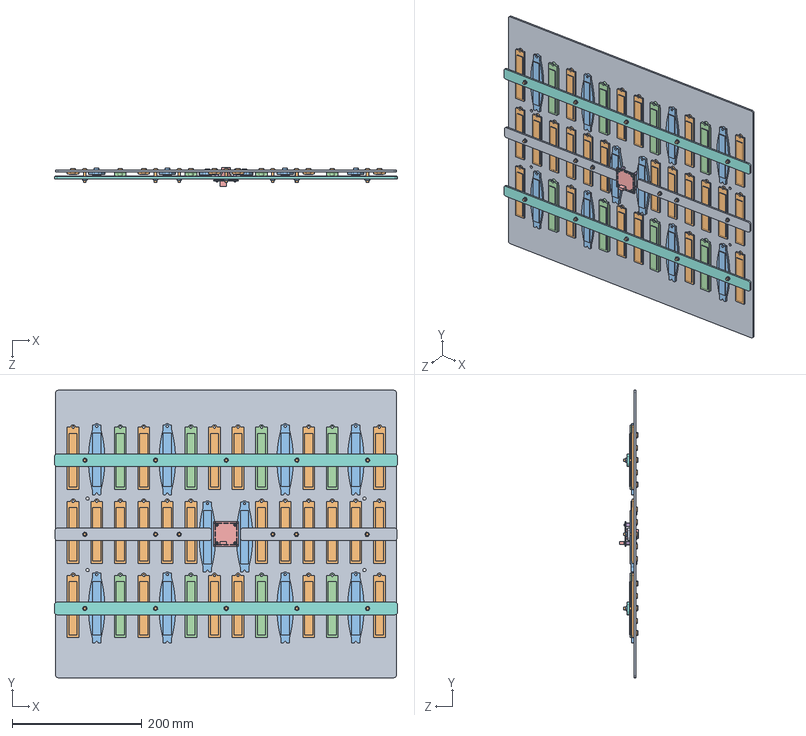
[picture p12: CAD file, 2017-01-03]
CAD/GrabCAD/OpenAG-Personal-Food-Computer-V2/light_panel_assembly/light_panel_assembly.SLDASM
528.8 x 443.3 x 29.5 mm
light_panel
ge_light_red x 24
ge_light_white x 10
ge_light_blue x 8
ELP_cam
2-56 .5in .1875 female-female standoff x 4
S-002-025-BTN-H-SS-001-256x1_4-button-head-screw x 8
light_strap x 2
light_strap_short x 2
S-008-075-BTN-H-SS-001-832x3_4-button-head-screw x 16
S-008-NUT-SS-001_832-SS-Nut-3-32thk x 16

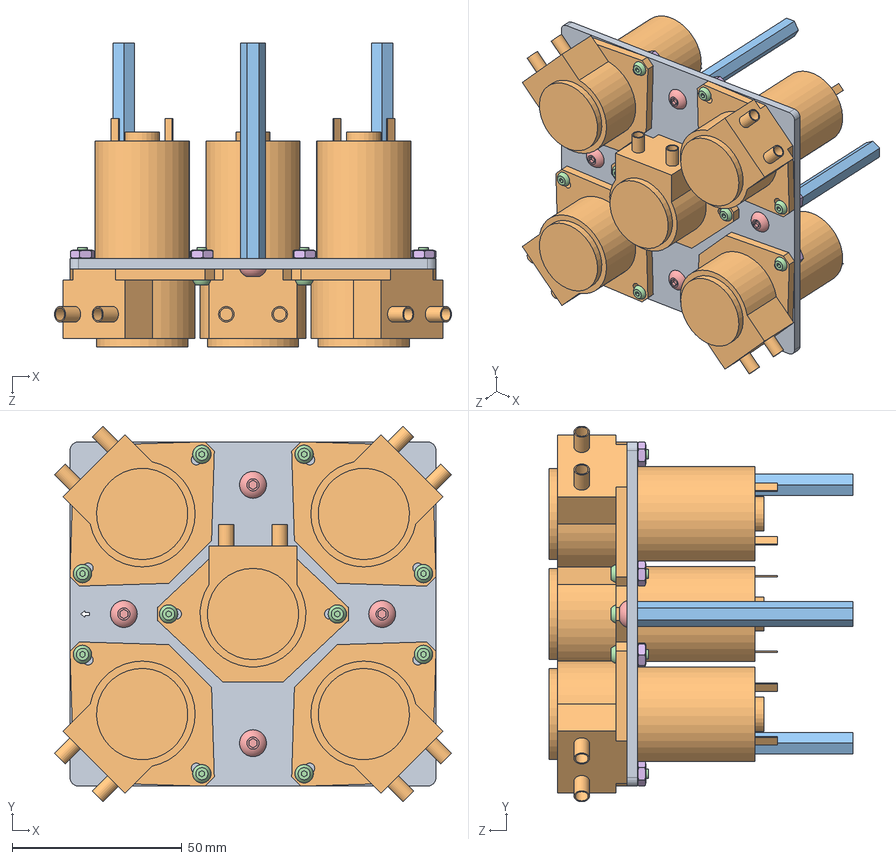
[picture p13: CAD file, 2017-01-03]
CAD/GrabCAD/OpenAG-Personal-Food-Computer-V2/pump_manifold/pump_assembly.SLDASM
117.1 x 110.8 x 89.7 mm
pump_mount02
water_pump x 5
8-32x2p5_standoff_f-f-PFC-HRD-0008 x 4
S-004-038-BTN-H-SS-001-440x3_8-button-head-screw x 10
S-008-038-BTN-H-SS-001-832x3_8-button-head-screw x 4
S-004-NUT-SS-001-440-SS-Nut-3_8thk x 10

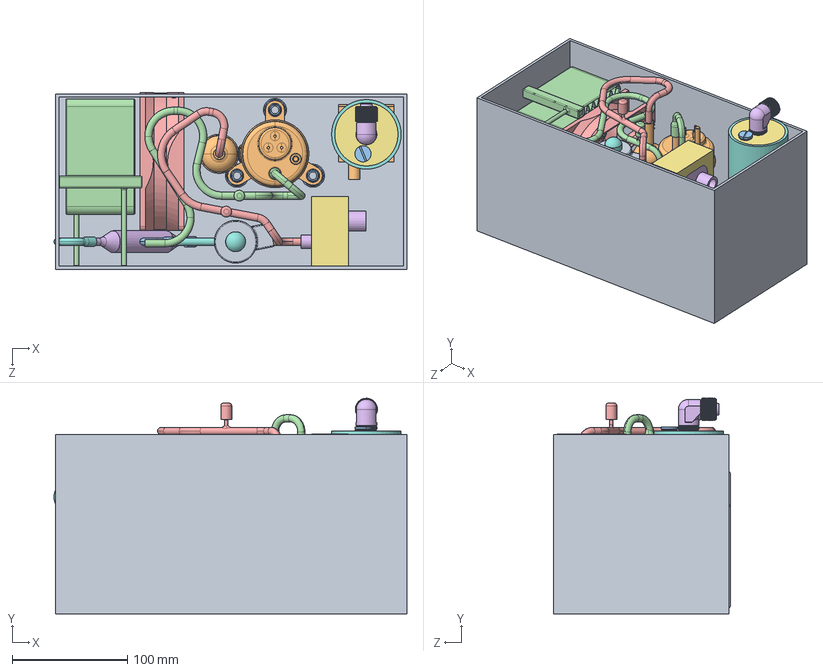
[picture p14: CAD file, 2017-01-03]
CAD/GrabCAD/OpenAG-Personal-Food-Computer-V2/SamsungFoodChiller.SLDASM
305.9 x 186.9 x 153.6 mm
12-6-6-Box
UX0T011ZNAE5
Grommet Isolator x 3
YIT Condenser
Fan-120mm Irwin
BC02-16
Top Cap Insert
Tank Main
Bottom Cap
Pump
Bitspower_G14-Plug
base 90_2
base 90
ring alphacool 90 13.10
Fujikoki Valve Body
Fujikoki Coil
EvapInlet
CondenserOutlet
CompressorOutlet
CompressorInlet
FilterDryer
InsulationMiddle
FilterDryerInlet

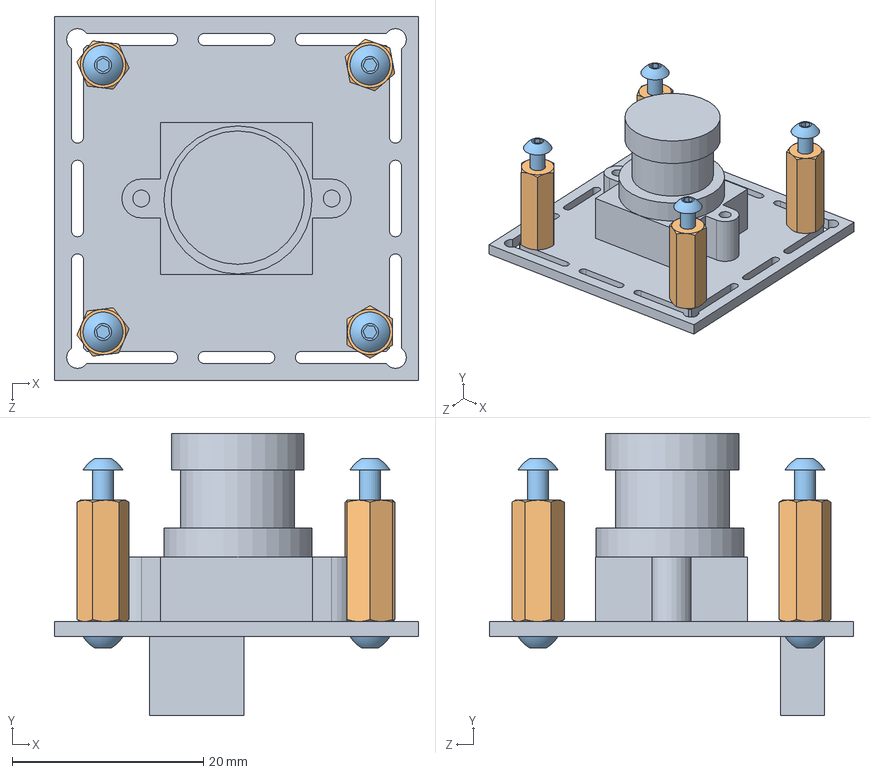
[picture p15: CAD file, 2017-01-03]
CAD/GrabCAD/OpenAG-Personal-Food-Computer-V2/sensor_assembly/ELP_cam_assembly_lightpanel.SLDASM
38.1 x 29.5 x 38.1 mm
ELP_cam
2-56 .5in .1875 female-female standoff x 4
S-002-025-BTN-H-SS-001-256x1_4-button-head-screw x 8

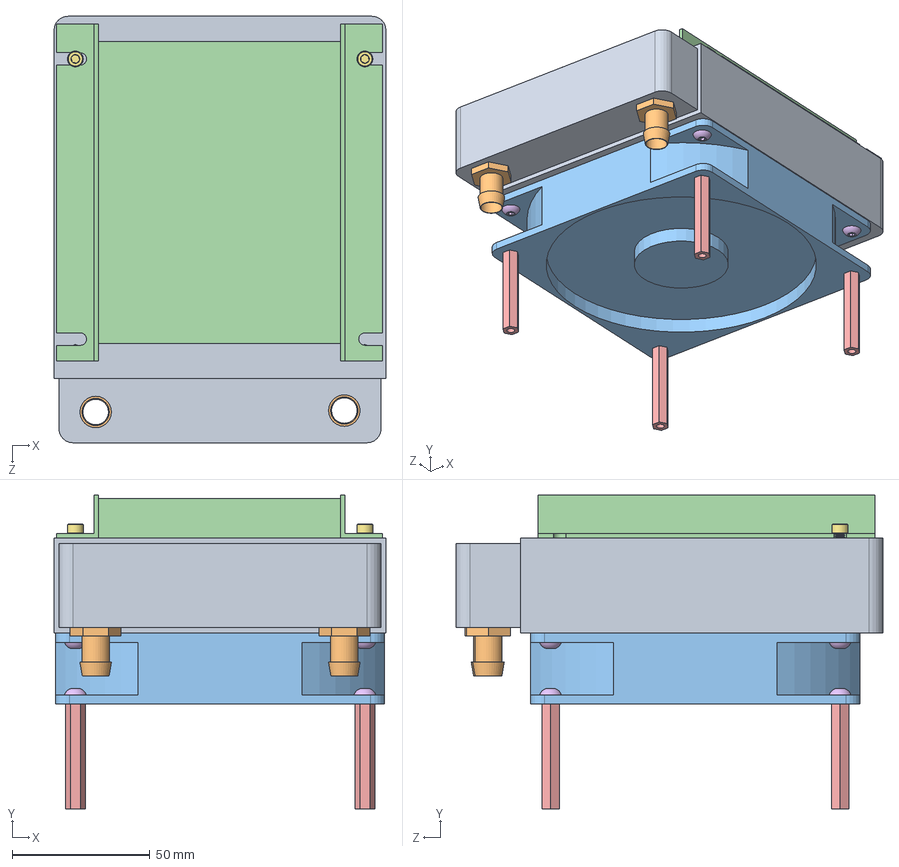
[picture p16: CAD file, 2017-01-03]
CAD/GrabCAD/OpenAG-Personal-Food-Computer-V2/Temperature Control Assembly/Temperature Control Unit.SLDASM
120.4 x 113.9 x 154.7 mm
temp_exchanger
G25_375_barb x 2
120mm_fan
Electric Heater
S-008-150-STD-O-AL-001_8-32_standoff_f-f_p25hex x 4
S-008-038-BTN-H-SS-001-832x3_8-button-head-screw x 8
6-32_screw03 x 2

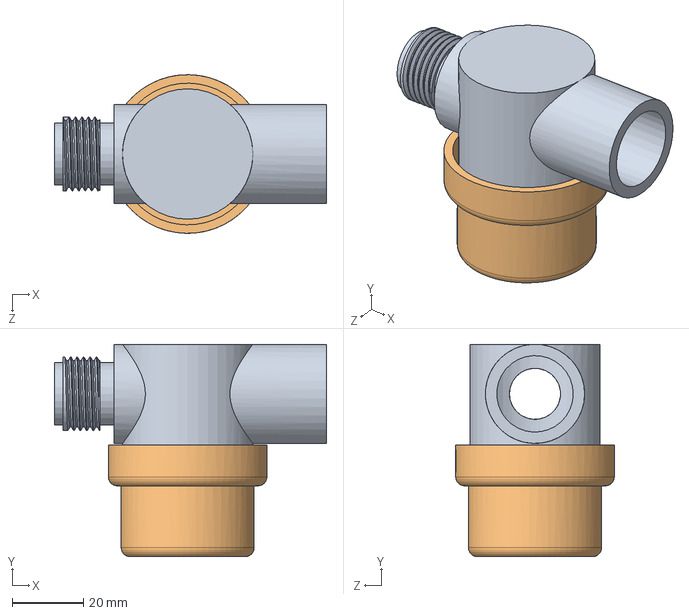
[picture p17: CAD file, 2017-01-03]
CAD/GrabCAD/OpenAG-Personal-Food-Computer-V2/water_manifold/Filter Assembly.SLDASM
76.2 x 59.5 x 44.4 mm
Filter Body
Filter cup

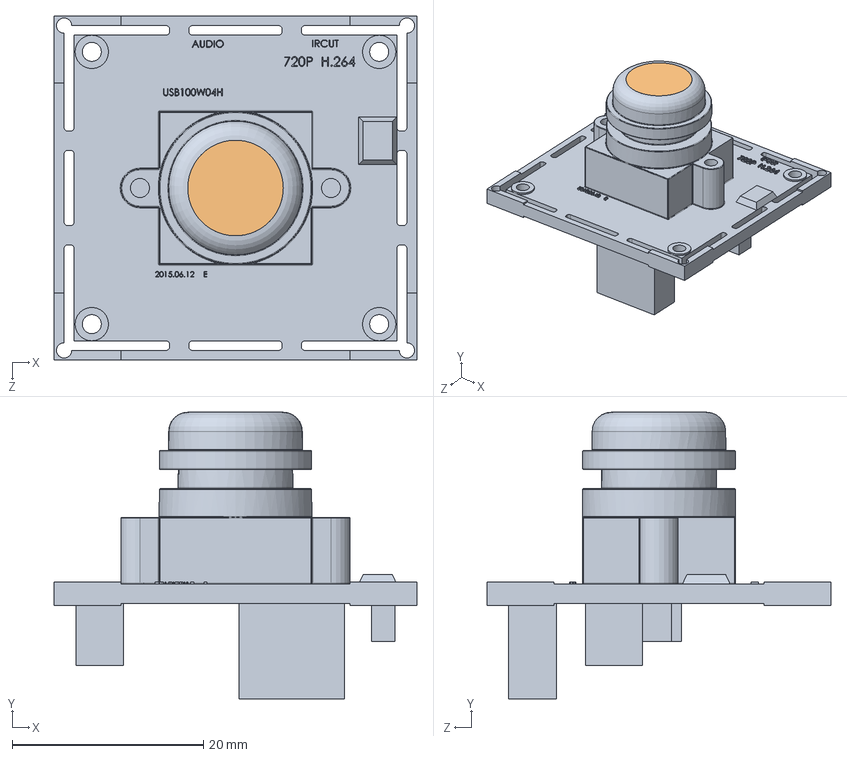
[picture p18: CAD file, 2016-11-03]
CAD/GrabCAD/OpenAG-Personal-Food-Computer-V2/web cam/Assem1cam.SLDASM
38.0 x 30.0 x 36.0 mm

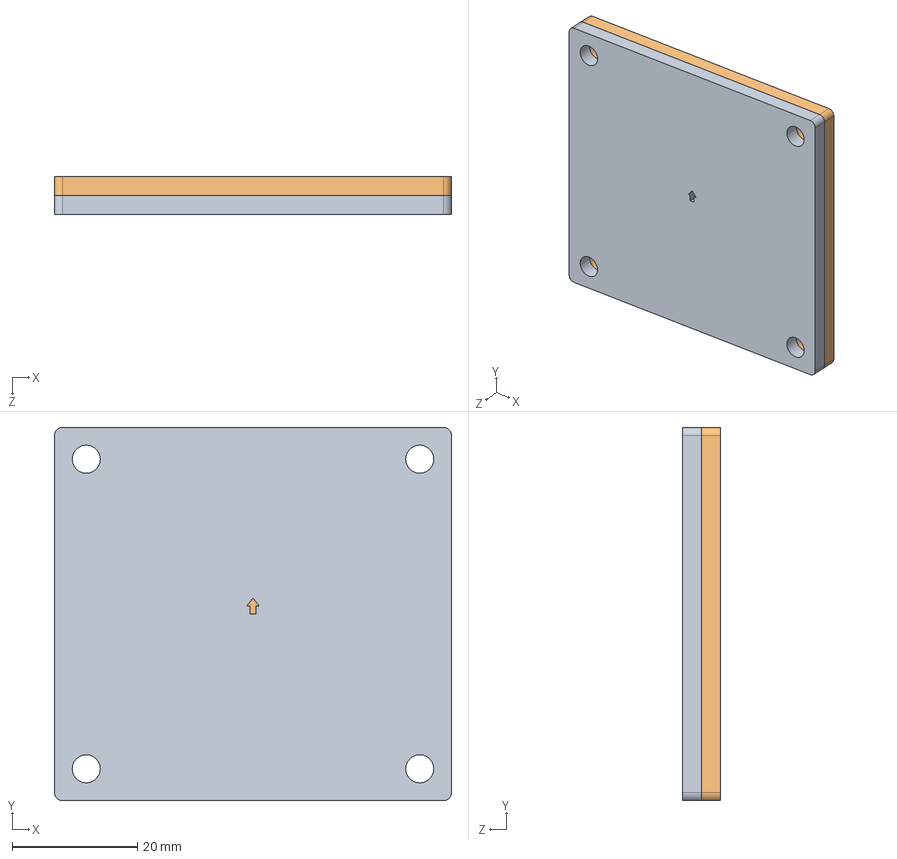
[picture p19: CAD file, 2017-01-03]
CAD/GrabCAD/OpenAG-Personal-Food-Computer-V2/Wire Pass Through/Wire Pass Through Plate.SLDASM
63.5 x 59.7 x 6.15 mm
Pass Through Back Plate
Pass Through Back Rubber Rubber Sheet

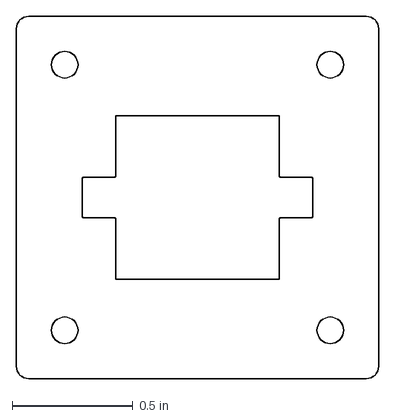
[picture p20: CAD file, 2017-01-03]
CAD/GrabCAD/DXF/Foam/ELP_cam_Foam.DXF
1.50 x 1.50 in

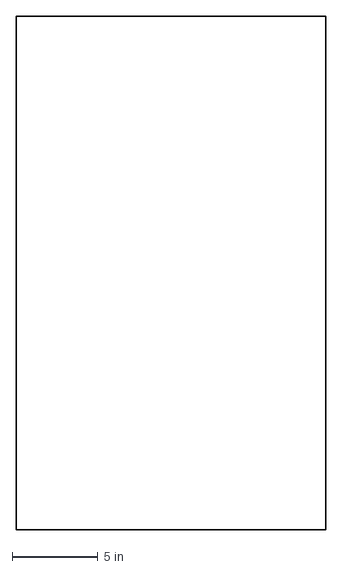
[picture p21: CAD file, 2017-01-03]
CAD/GrabCAD/DXF/Insulation/Outer side panel insulation.DXF
18.0 x 29.9 in

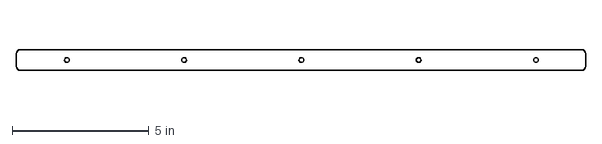
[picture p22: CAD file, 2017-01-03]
CAD/GrabCAD/DXF/Opaque/Light Manifold/light_strap.DXF
20.8 x 0.765 in

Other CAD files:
CAD/GrabCAD/OpenAG-Personal-Food-Computer-V2/Tank Main.sldprt
CAD/GrabCAD/DXF/Opaque/Outer Skins/outer-top-plate.DXF
CAD/GrabCAD/DXF/Foam/Pass Through Back Rubber Sheet.DXF
CAD/GrabCAD/DXF/Foam/Pass Through Front Rubber Sheet.DXF
CAD/GrabCAD/DXF/Insulation/Rearsheet insulation.DXF
CAD/GrabCAD/DXF/Insulation/inner-side-panel insulation.DXF
CAD/GrabCAD/DXF/Insulation/outer-top-plate insulation.DXF
CAD/GrabCAD/DXF/Opaque/Light Manifold/light_panel.DXF
CAD/GrabCAD/DXF/Opaque/Light Manifold/light_strap_short.DXF
CAD/GrabCAD/DXF/Opaque/Outer Skins/outer-side-panel.DXF
CAD/GrabCAD/DXF/Opaque/Outer Skins/rearsheet.DXF
CAD/GrabCAD/DXF/Opaque/Pass Through Back Plate.DXF
CAD/GrabCAD/DXF/Translucent 1/Brain Manifold/brain_manifold.DXF
CAD/GrabCAD/DXF/Translucent 1/Brain Manifold/pi-mount-2.DXF
CAD/GrabCAD/DXF/Translucent 1/Chiller base plate.DXF
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

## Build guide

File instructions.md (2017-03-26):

# PFC2 Build Instructions

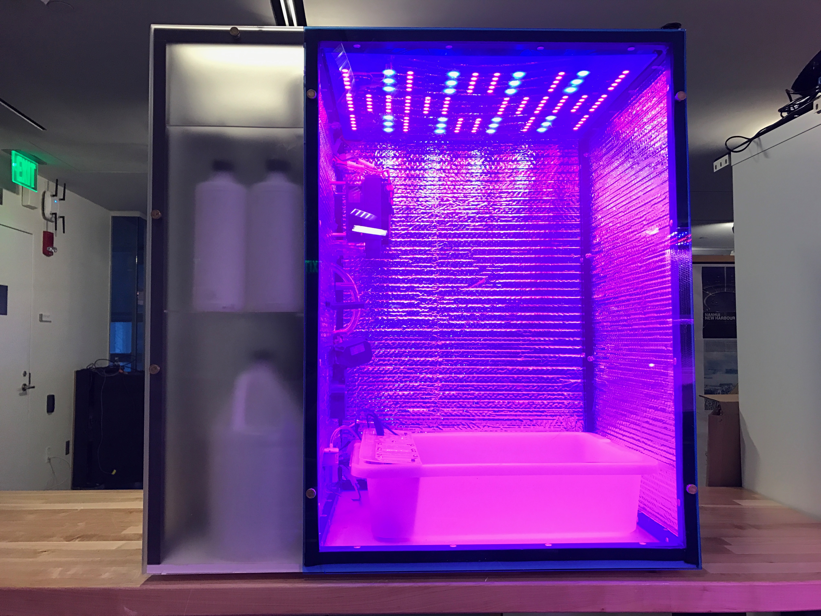
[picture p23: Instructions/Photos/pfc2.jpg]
pfc2


## Before you begin:
Printing Out the [Bill of Materials (BOM)](./BOM/BOM_MASTER.xlsx) is helpful as a reference. The descriptions it contains help distinguish between parts.
Download the CAD documents from [here](CAD/GrabCAD) to be viewed in e-drawings-viewer.

## Submodule Build Instructions
Follow the directions to assemble each submodule. Each submodule can be assembled in parallel, but some will take longer than others to complete.

- [Frame](./Instructions/frame.md)
- [Electronics Panel](./Instructions/electronics_panel.md)
- [Brain Module](./Instructions/brain_module.md)
- [Light Panel](./Instructions/light_panel.md)
- [Power Module](./Instructions/power_module.md)
- [Water Manifold](./Instructions/water_manifold.md)
- [Chiller](./Instructions/chiller.md)

## Set Electrical Components into Proper Modes
1. Set the **Multifunction Relay** into **Mode 10** and **Timer 1** to 20 seconds
1. Tune the **Pulse Generator** to **140Hz**
1. Set the **Atlas Circuits** into **I2C Mode**
1. On the **Signal Board** off solder points below both BNC Jacks and tape over w/electrical or kapton tape

## Mounting the Electronics panel
1. place the electronics panel in the partially assembled frame, as shown.<!-- TODO: Not shown --> Loosely fasten in place with a few **S-018-32-075-PST-F-AL(Bag 31)** binder posts along each side side.

## Mount chamber side components to the electronics panel
 1. Panel is mounted and the insulation is in place:
 1. Mount the Temperature Control Module, air flush out, and aeration pump to their resp[ective zones in the electronics panel.

## Mounting the Frame Top Section
1. Mount the Top section of the frame. Line up the Appropriate Frame connectors, gradually tapping each connector in a small amount with each hit.

## Mount the Power Supply Assembly
1. Mount the Power Supply Assembly to the top of the electical box using three **S-025-20-438-BTN-S-SS (Bag 26)** 1/4-20 screws.
1. Connect the power supply wires to the appropriate places on the brain manifold.

## Mounting the Body Panels
1. Mount the Rest of the Body panels. When aligning for mounting, notice the small etched markings indicating the orientation of the panel. Each of these markings faces inward, have an arrow and word to show orientation, and most line up with the marking of an adjacent panel.

## Final Integration
- Reference the CAD model for final integration and watch [the build video](https://youtu.be/Uf1FqjcPWsI)!

## Final Integration Notes
 - When installing the air temperature and humidity sensor, wrap a piece of electrical tape around the base so it makes a snug fit with the mount.

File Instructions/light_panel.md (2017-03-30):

## Assemble the Light Panel
* *WARNING! Tightening light straps before each row of lights is finished may cause a strap to break.*
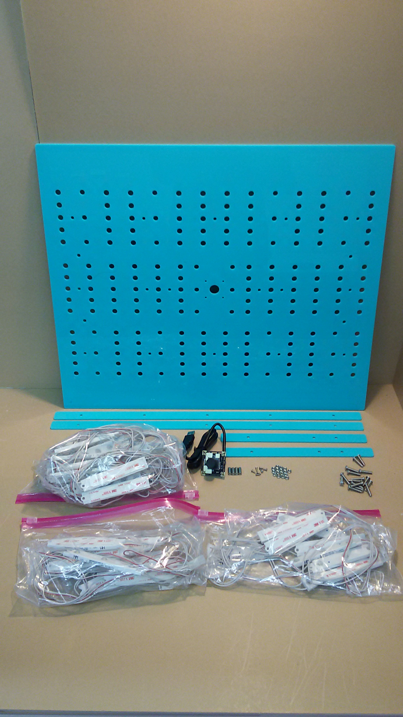
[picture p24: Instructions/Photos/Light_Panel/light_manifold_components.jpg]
Light Panel Components
 

1. See **Sub-Assembly BOM's** **"Light Manifold"** tab for a complete list of parts.
2. On Acrylic Light Panel **STR-PNL-0006**, locate the small etching at the corner of the piece. This is the top of the panel.
3. With the etching at near left corner, Populate the 5 small holes in the first row with 8-32x0.75" bolts.
4. Begin the pattern of the LED strands from their connectorized ends at the near right corner, see above pattern for placement.
5. See this picture for an overview of the LED panel orientation and refer to here as you continue. The numbers for the other colors can be found under `Instructions/Photos/Light_Panel/[blue|red]_led_routing_8in.png`:
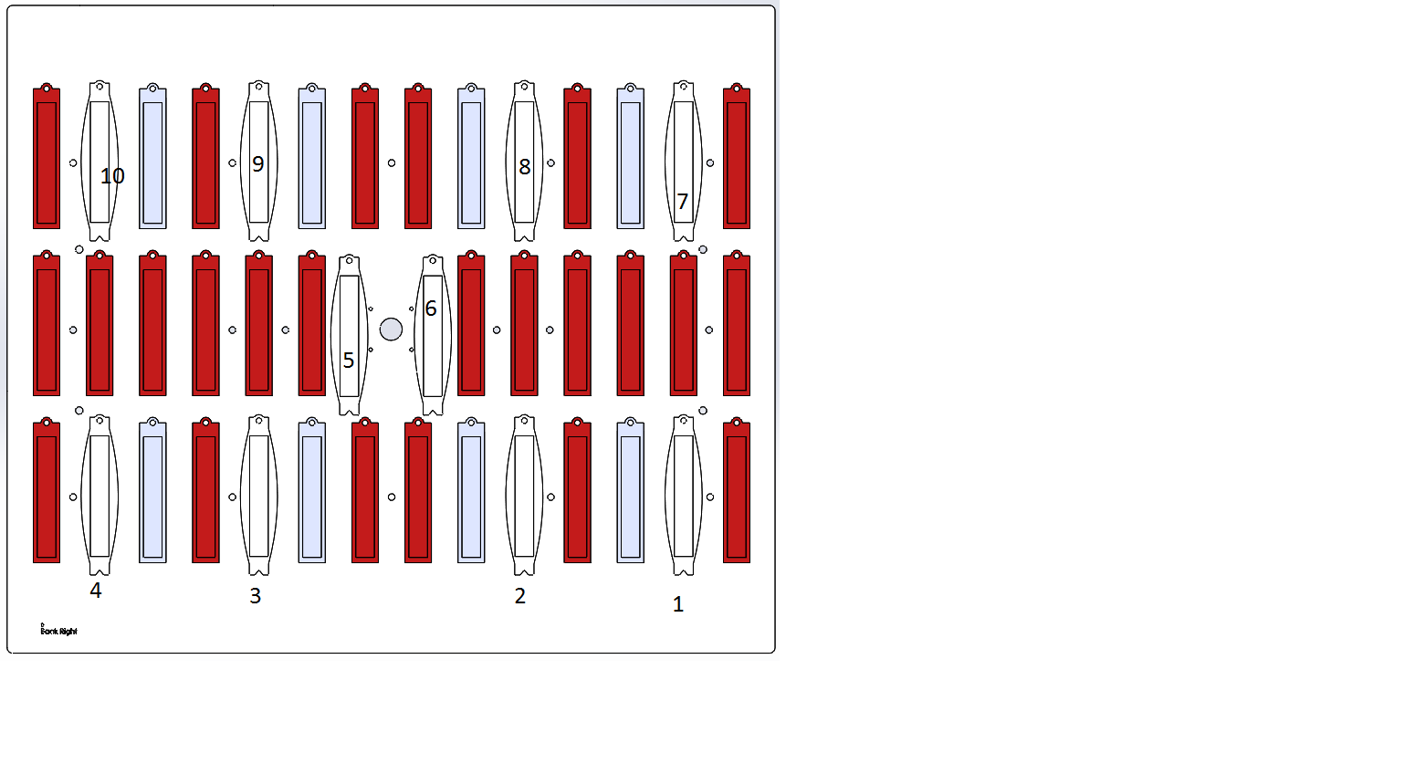
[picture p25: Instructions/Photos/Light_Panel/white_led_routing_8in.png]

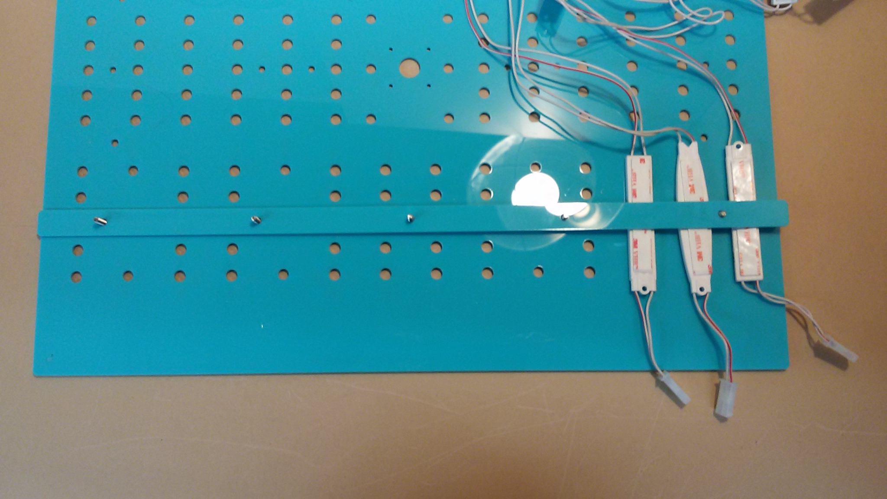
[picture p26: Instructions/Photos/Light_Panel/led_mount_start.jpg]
LED Mounting start picture
5. Fit the longer light strap **STR-PNL-0011** to the bolt pattern. Thread one **S-#08-32-094-NUT-H-SS (Bag 6)** nut onto the 8-32x0.75 **S-#08-32-075-BTN-S-SS (Bag 4)** screw between the red & white LED's. Only turn the nut 1-2 times- Tightening nuts before finishing this row may break a strap.  
6. Begin populating the patterned holes to the left according to the above schematic. Loosly thread nuts onto the bolts aft each section.
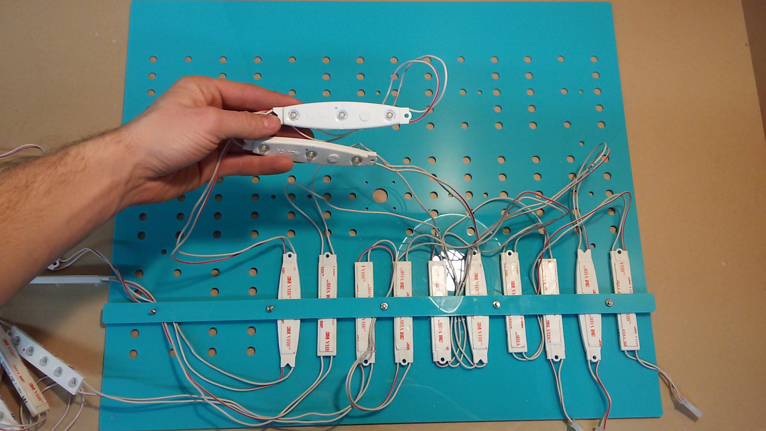
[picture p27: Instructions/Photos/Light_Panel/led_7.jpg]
PIC LED 7
7. For the White LEDs, skip two as shown Here:  These will populate the middle row.
8. Populate the middle row via the same method, following the schematic.
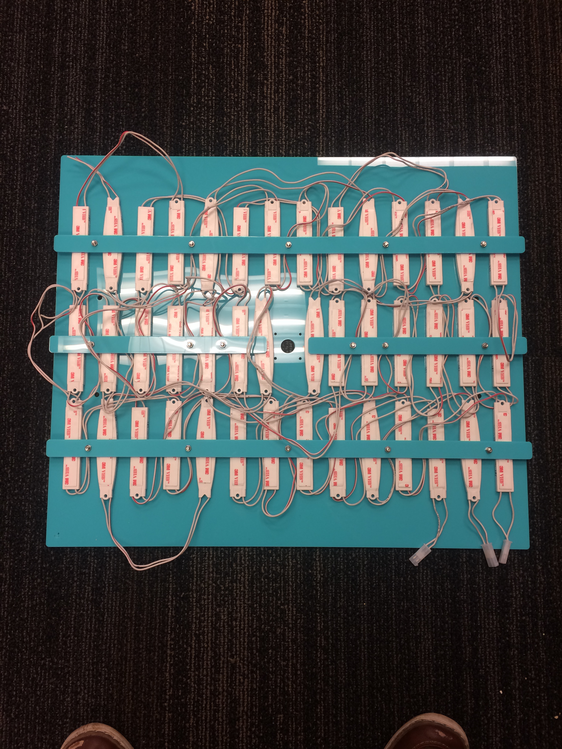
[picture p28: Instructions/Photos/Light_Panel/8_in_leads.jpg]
Finished Top Side
9. The in the final Row, start on the left with the Last LED of the red strand, Moving right as you populate the row. 
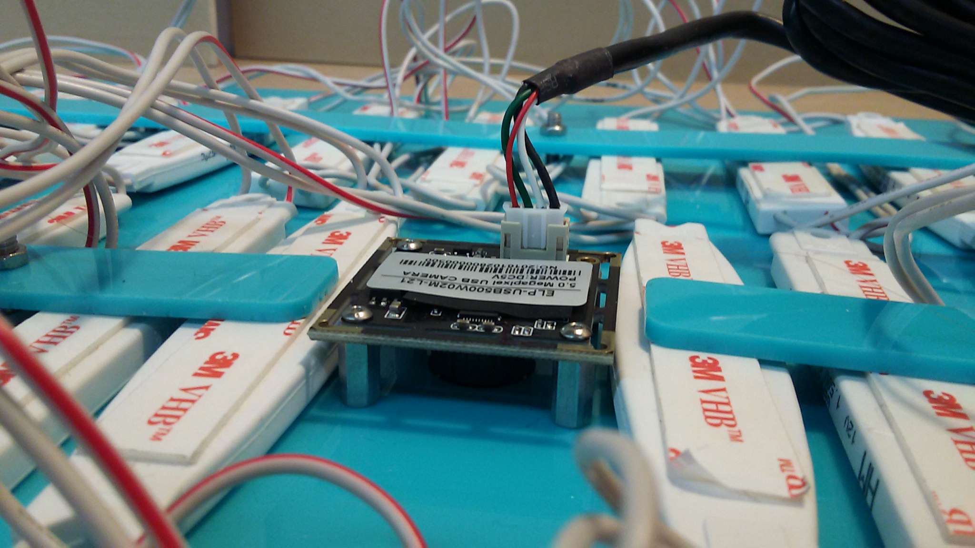
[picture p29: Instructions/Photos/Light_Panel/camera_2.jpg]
Camera Mounting
10. Mount the camera to the light panel using the supplied x4 **S-#02-56-050-STD-H-AL-FF (Bag 19)**, x8 **S-#02-56-025-BTN-S-SS (Bag 21)**, and the **SEN-PRB-0005** camera. Orient the camera so the connecector is closest to the LED string connectors.

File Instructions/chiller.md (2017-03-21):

## Chiller Assembly.
 * *The chiller arrives itself with a list of components: Chiller Submodule, compressor driver electronics, rubber grommets, and black  Heat Exchanger insulation. *
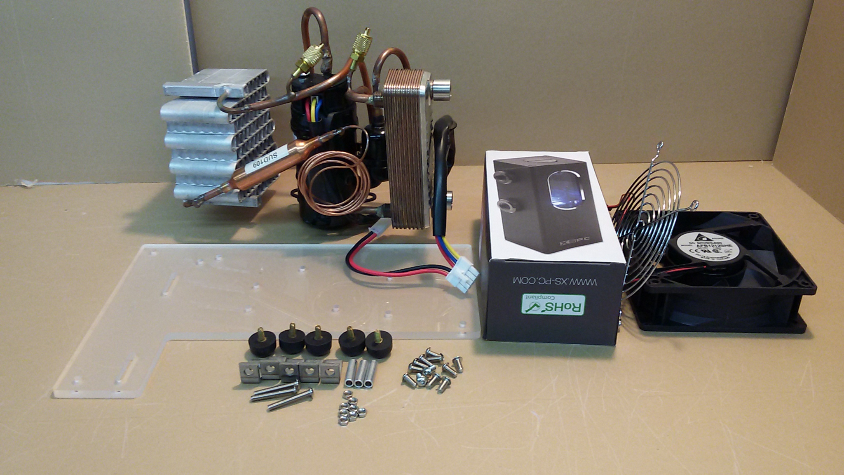
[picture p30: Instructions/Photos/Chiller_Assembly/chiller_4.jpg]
 
 **Baseplate mounting placement diagrams**
 1. Mount 5 rubber feet and two L brackets to the baseplate. The Two L-Brackets are placed on the top side of the acryllic plate when it is placed in the shape of an "L".
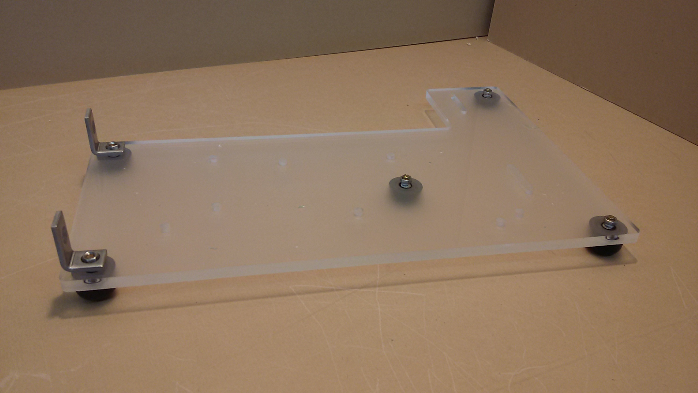
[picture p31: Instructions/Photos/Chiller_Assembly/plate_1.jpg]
Rubber Feet
 
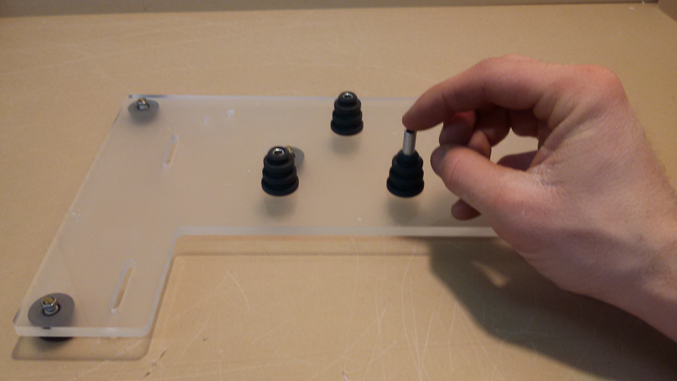
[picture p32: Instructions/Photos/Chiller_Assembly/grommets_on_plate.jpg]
Foot Mounting Pattern
 2. The compressor mounted to its baseplate via x3 **S-#08-00-875-SPC-O-AL (Bag 38)**, x3 **S-#08-32-150-BTN-S-SS (Bag 8)**, and x3 **S-#08-32-094-NUT-H-SS　(Bag 6)**. Push the small end of the rubber grommet to the compressors tabs, slide in the metal spacers, and bolt the compressor in place using the **S-#08-32-150-BTN-S-SS (Bag 8)** 8-32 Bolts. 
 3.  On the copper Heat Exchanger, mount the black insulation.
 4. Mount the Guard to the Fan- This side will face the aluminum heat exchanger once mounted.
 5. Mount the Fan to the L-Brackets.
 6. Thread two **ACT-FTG-0001** into the Side of the pump that has two ports.
 7. Thread two **ACT-FTG-0001** into the Copper colored Heat Exchanger
 8. Mount the Ion Pump/Resevoir to the Baseplate
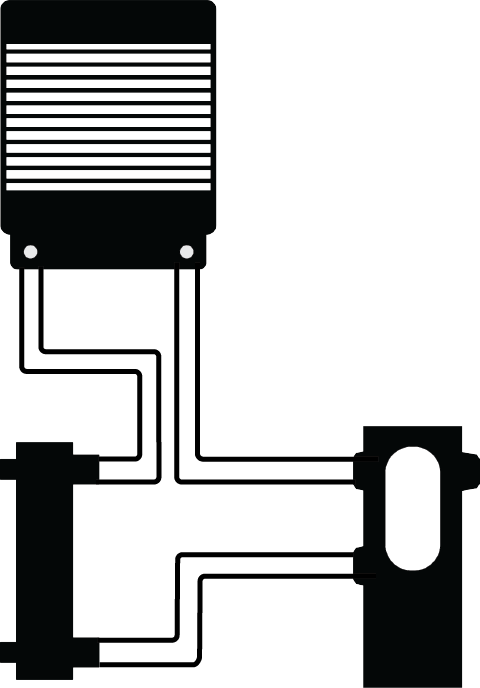
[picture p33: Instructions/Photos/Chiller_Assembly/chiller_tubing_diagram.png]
Chiller Tubing Diagram
 9. Measure and cut 3 piece of the thicker tubing to the fit the pattern in the following diagram: 
 Make sure to leave enough length to remove the chiller from the PFC while running, & place two hoseclamps over each hose before connecting to any barbs.
 10. Once cut to length, firmly press the hoses over their barbs and tighten the hoseclamps over the barbs.
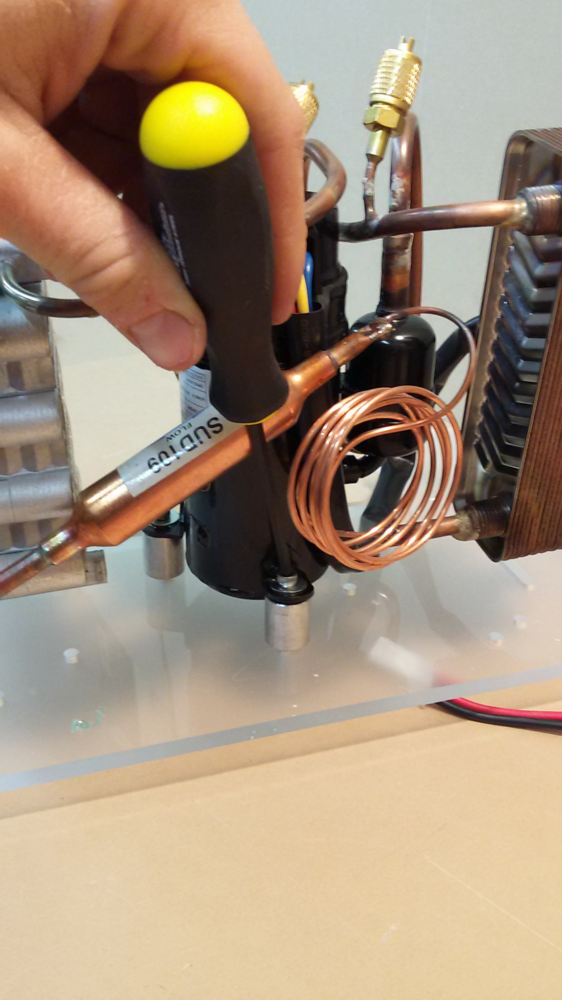
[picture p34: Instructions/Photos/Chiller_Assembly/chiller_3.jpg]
Chiller Picture
 11. Put the Chiller Assembly in its place. (Beta prototype models will have a tight fit)

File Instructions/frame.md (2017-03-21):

<!-- TODO: Indicate significance of threading -->
<!-- TODO: Identify chirarity and parts, the things that were confusing. -->
## Assemble the Frame
### Tools
 - tape measure
 - Rubber Mallet
 - Table
 - 1/4" Flat head Screwdriver

 1. Check that your kit has all the proper frame bars & connectors. In **BOM_Master**, See the **STR-BAR-PCK-0001** & **"Kit Stage 1 BOM"** tab for a list of bars, and connectors. (STR-CON-0001, STR-CON-0002, STR-CON-0003)
 2.  Set the baseplate to the side for now, and group the bars by length
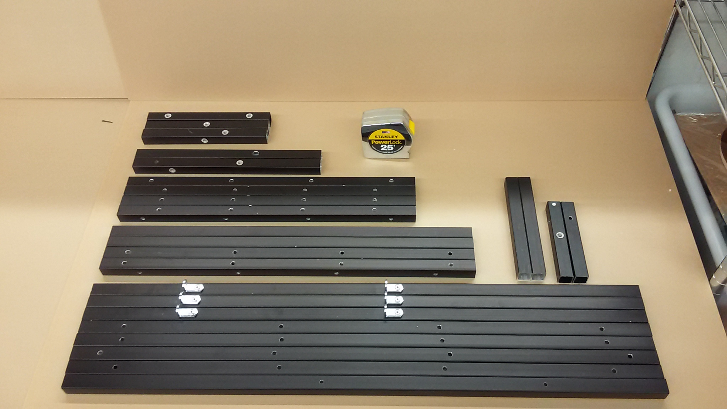
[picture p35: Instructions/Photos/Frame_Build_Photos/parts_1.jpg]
Sorted Bars
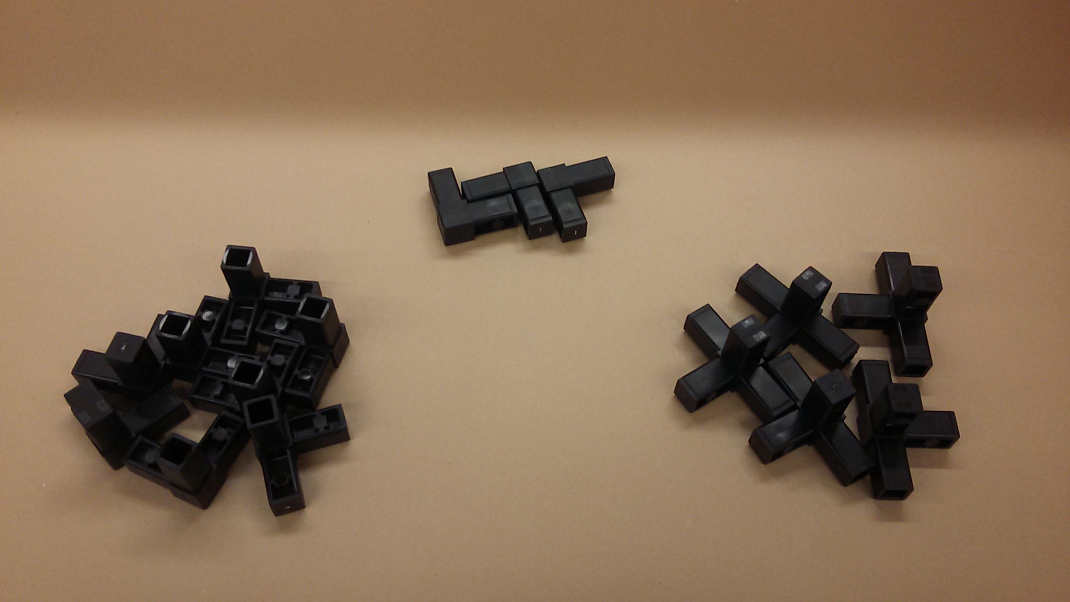
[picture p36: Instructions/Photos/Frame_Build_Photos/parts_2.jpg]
connectors
 

#### Base Layer

1. Collect the Base Layer Components:
  * x2 of STR-BAR-0001 	(18" 	Bar)
  * x1 of STR-BAR-0003 	(21.25" Bar [Holes on all sides])
  * x1 of STR-BAR-0004	(8.25" 	Bar)
  * x1 of STR-BAR-0005	(12"	Bar)
  * x1 of STR-BAR-0006	(5.25"	Bar)
  * x1 of STR-BAR-0007	(7"		Bar)
  * x1 of STR-BAR-0008	(21.25"	Bar [Holes on 2 sides])
  * x4 of STR-CON-0001 	(3-Way Connector)
  * x2 of STR-CON-0002 	(4-Way Connector)
  * x2 of STR-CON-0003 	(2-Way Connector)

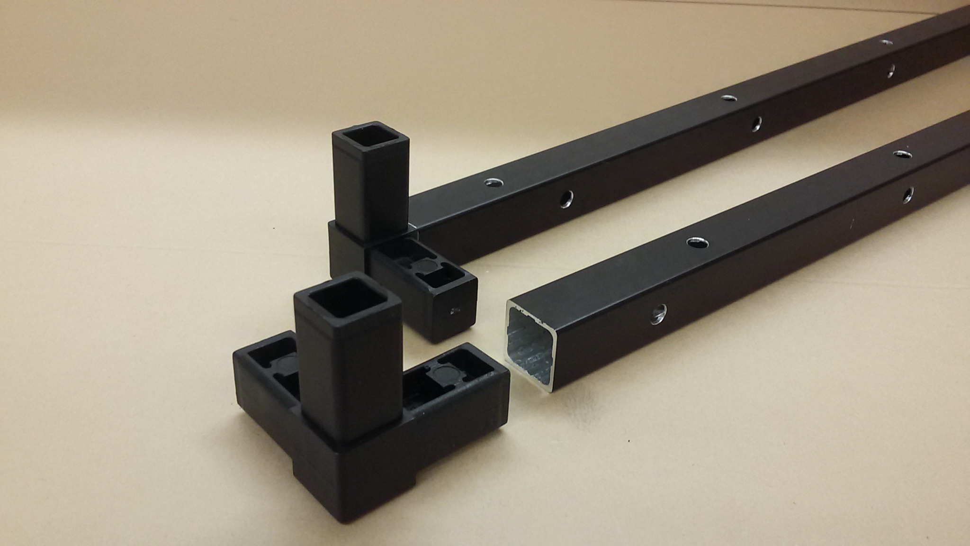
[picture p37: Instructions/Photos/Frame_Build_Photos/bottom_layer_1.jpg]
STR-BAR-0001 with STR-CON components.
2. In x1 **STR-BAR-0001** bar, Insert x2 **STR-CON-0001** connectors. In The other **STR-BAR-0001**, insert x1 **STR-CON-0001** and x1 **STR-CON-0002**. Wider hole spacing should be on the vertical surface in the final assembly. These bars line the bottom side of the grow chamber. 
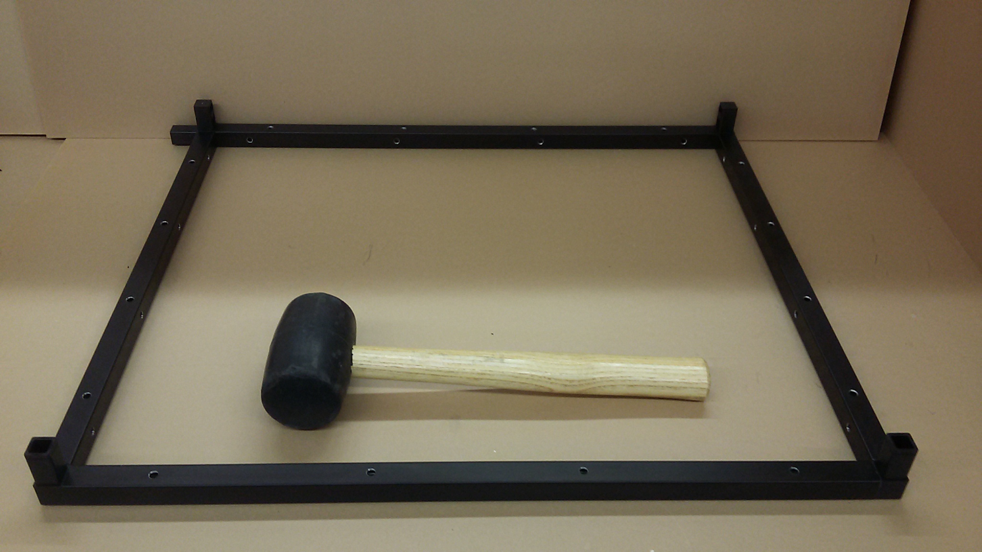
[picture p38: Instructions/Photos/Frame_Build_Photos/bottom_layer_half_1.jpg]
Grow Chamber portion of bottom layer.
3. Lay down one **STR-BAR-0003** in back, and one **STR-BAR-0008** in front. The wider hole spacing of **STR-BAR-0003** should be on the vertical surface. Make sure the 4-way connnector **STR-CON-0002** is in the far left corner. Some *light* force may be required here. Set This Assembly to the side. 
4. Gather x1 of: **STR-BAR-0004**, **STR-BAR-0005**, **STR-BAR-0006**, **STR-BAR-0007**.
5. Connect x1 of **STR-CON-0001**  and x1 of **STR-CON-0002** into **STR-BAR-0005**, in orientation shown below.
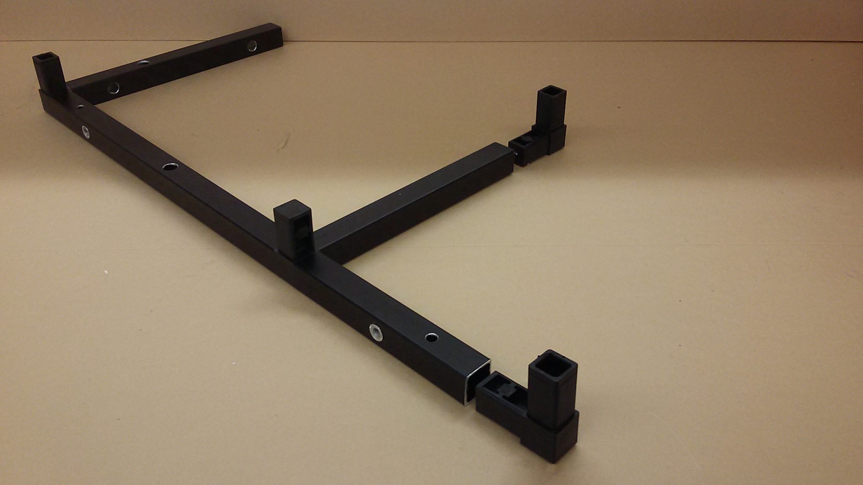
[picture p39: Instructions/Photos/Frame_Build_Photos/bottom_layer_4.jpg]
Electric Box Portion of Bottom Layer.
6. Connect **STR-BAR-0004** onto the 3-way connector, wider hole spacing vertical on the vertical surface, **STR-BAR-0007** perpendicular on the 4-way connector, and **STR-BAR-0006** parallel, with holes oriented as shown.
7. Press the **STR-CON-0003** connectors into the ends of **STR-BAR-0007** & **STR-BAR-0006**.
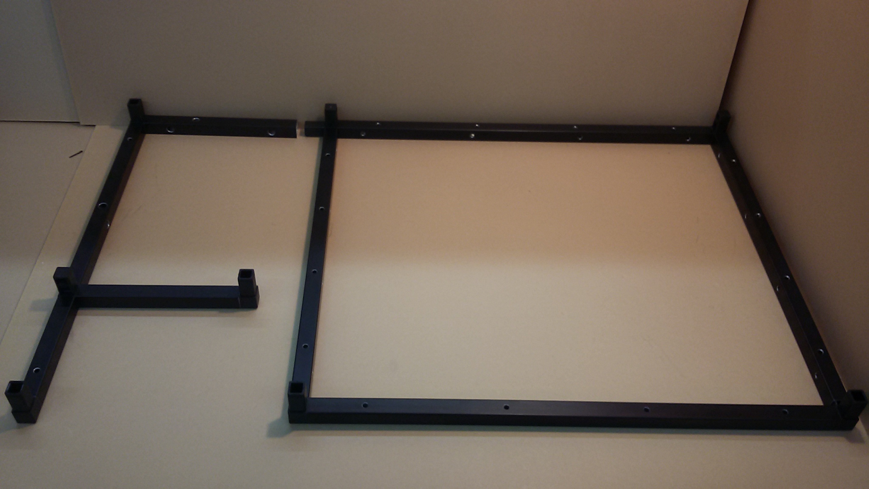
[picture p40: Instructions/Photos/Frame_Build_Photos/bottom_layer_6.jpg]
Final step of bottom layer assembly
8. Double check all bar orientations, then attach the two assemblies together. 

### Mount Frame to Base Plate
1. The Frame is mounted to the baseplate with **S-018-32-075-PST-F-AL (Bag 31)** Binder post. The countersunk holes of the baseplate should face down.

### Mounting Vertical Members
1. There are three vertical members: **STR-BAR-0002**, **STR-BAR-0009** & **STR-BAR-0010**
  * Refering to **BOM-Master's STR-BAR-PCK-0001**,
  * **STR-BAR-0010** has L-brackets attached to it, with two larger holes on the bottom.
  	* One of the **STR-BAR-0010** does not have L-Brackets, but has threads.
  	* One of the **STR-BAR-0010** with L-brackets has threads, but the other 2 do not.
  * **STR-BAR-0009** has 10 holes, including Threads for the door attachement
  * **STR-BAR-0002** has 16 holes, and stands in the Rear of the growing chamber.
2. Attach all **STR-BAR-0010** to the Electronics Box side- the smaller bottom half.
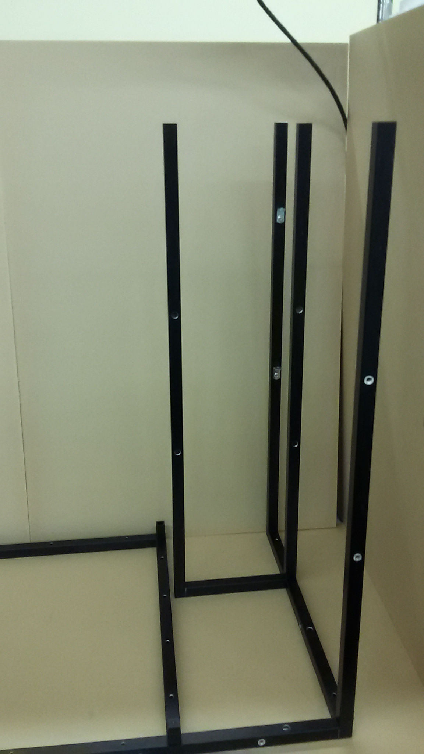
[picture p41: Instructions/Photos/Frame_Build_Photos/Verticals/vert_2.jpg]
**STR-BAR-0010** Orientations
	* Take note of the thread orientation:  <!-- TODO: Rotate image -->
3. Attach both **STR-BAR-0002** to the back two connectors of the growing chamber, wider hole spacing toward back. *Attention:* This bar is not symmetric. There is a top & bottom. How to tell: <!-- TODO: HOW TO TELL -->
4. attach both **STR-BAR-0009** to the front two connectors, threaded holes facing outward.
 * It is good practice to check Acrylic panel alignment before continuing. **STR-BAR-0002** is designed to be symetric, hoever small variations in machining caould cause misaligned holes.

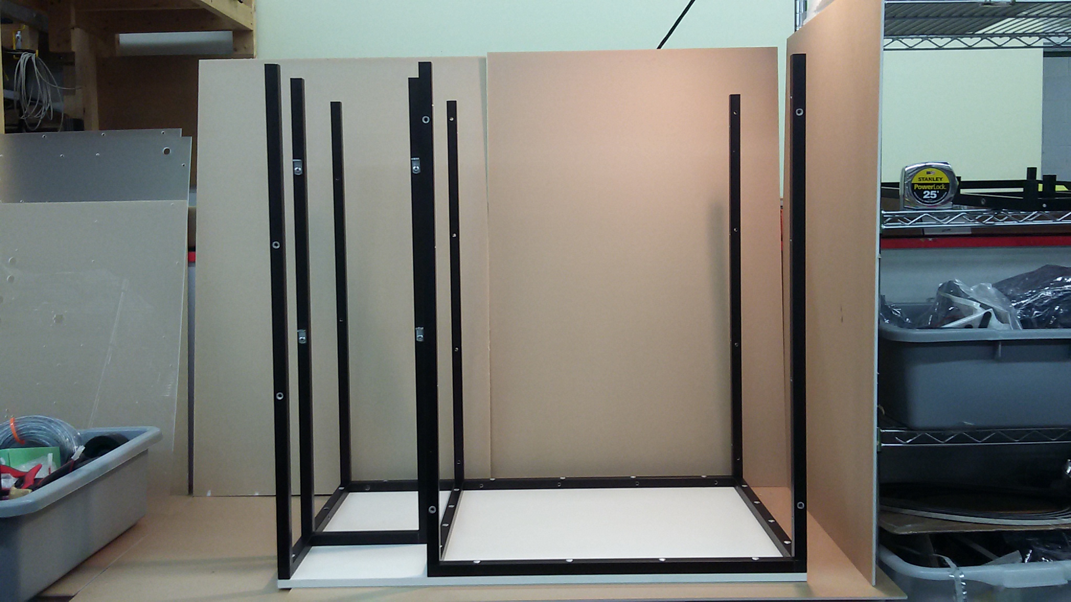
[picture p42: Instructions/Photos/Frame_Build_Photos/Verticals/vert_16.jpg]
Vertical Bars in their places.


#### Top Layer

- **STR-BAR-0001** x2
- **STR-BAR-0003** x1
- **STR-BAR-0004** x2
- **STR-BAR-0005** x1
- **STR-BAR-0006** x1
- **STR-BAR-0007** x1
- **STR-BAR-0008** x1
- **STR-CON-0001** x4
- **STR-CON-0002** x3
- **STR-CON-0003** x1

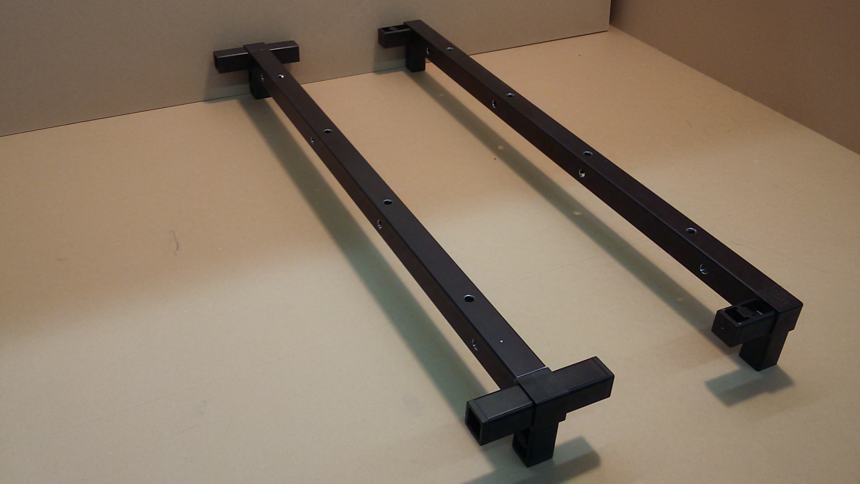
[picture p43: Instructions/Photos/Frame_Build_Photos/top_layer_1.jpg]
Top Side Bars of Growing Chamber
1. In one **STR-BAR-0001** bar, Insert x2 **STR-CON-0001** connectors. In The other **STR-BAR-0001**, insert x2 **STR-CON-0002**. Wider hole spacing should be through the vertical surface of each bar, as shown. These bars line the top side of the grow chamber.
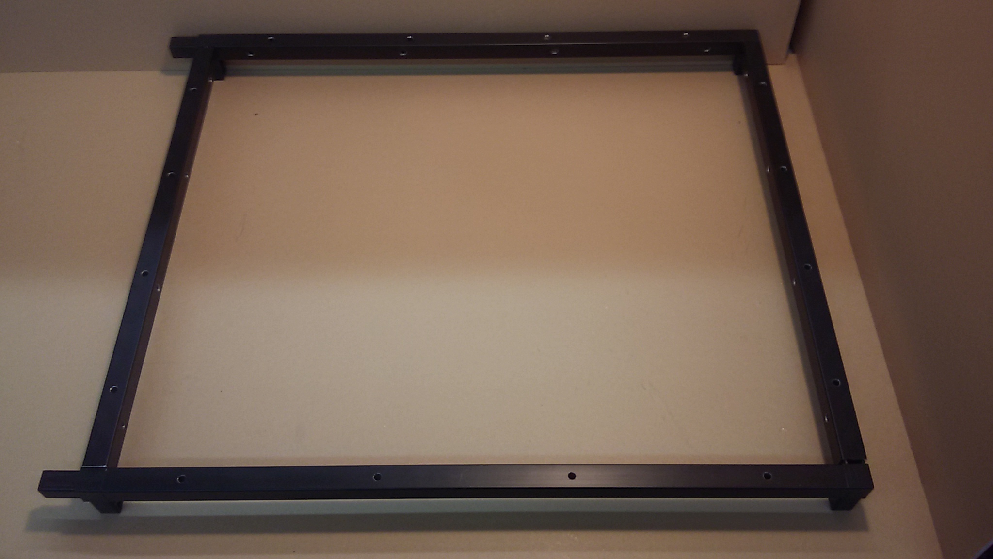
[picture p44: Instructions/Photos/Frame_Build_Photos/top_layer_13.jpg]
Growing Chamber Half of Top Layer
1. Lay down one **STR-BAR-0003** in back, and one **STR-BAR-0008** in front. Again, the wider hole spacing on **STR-BAR-0003** should be on the vertical surface. Push the components together. Some *light* force may be necessary here.
1. Gather x2 of **STR-BAR-0004**, x1 of **STR-BAR-0005**, x1 of **STR-BAR-0006**, x1 of **STR-BAR-0007**, x2 of **STR-CON-0001**, x1 of **STR-CON-0002**, x1 of **STR-CON-0003**.
1. Connect x1 **STR-CON-0001**  and x1 **STR-CON-0002** into **STR-BAR-0005**, in orientation shown.
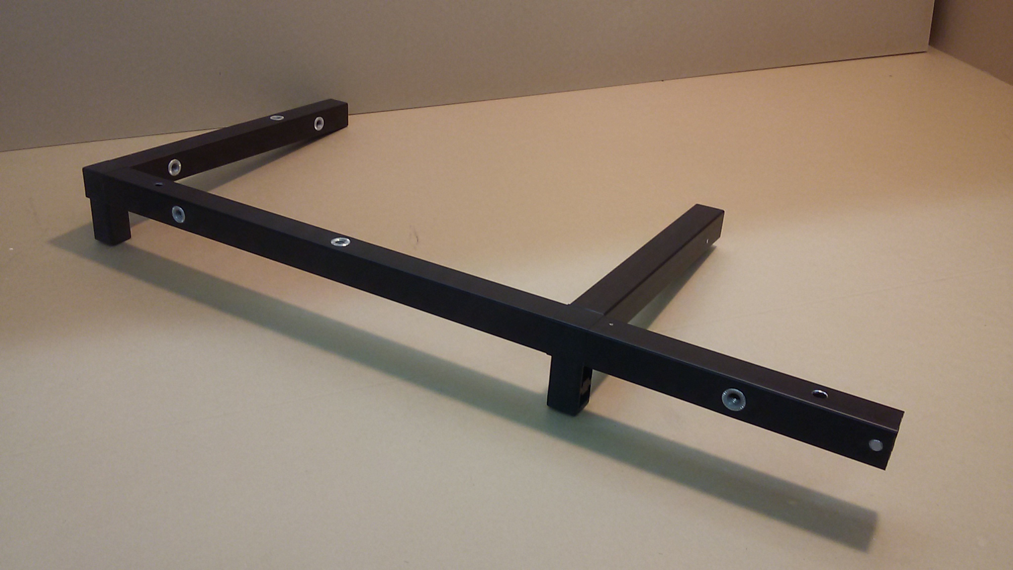
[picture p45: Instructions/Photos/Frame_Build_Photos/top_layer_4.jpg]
Step 4&5
1. Connect **STR-BAR-0004** onto the 3-way connector with holes oriented as shown, **STR-BAR-0007** perpendicular on the 4-way connector, and **STR-BAR-0006** parallel, with holes oriented as shown. 
1. Insert x1 **STR-CON-0003** in the end of **STR-BAR-0007** with the exposed end downward, x1 **STR-CON-0001** similarly into **STR-BAR-0006**.
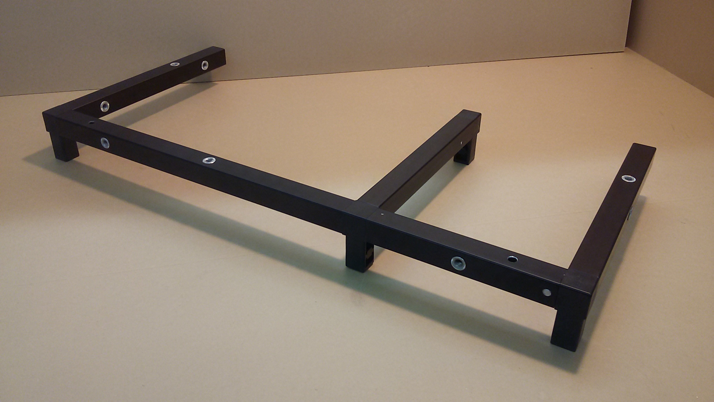
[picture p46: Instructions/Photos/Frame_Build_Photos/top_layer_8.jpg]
Electric Box Portion of Top Layer
1. Connect the final **STR-BAR-0004** horizontally on the 3 way connector. Centered thread through the outer vertical surface.
1. check orientations, attach halves.
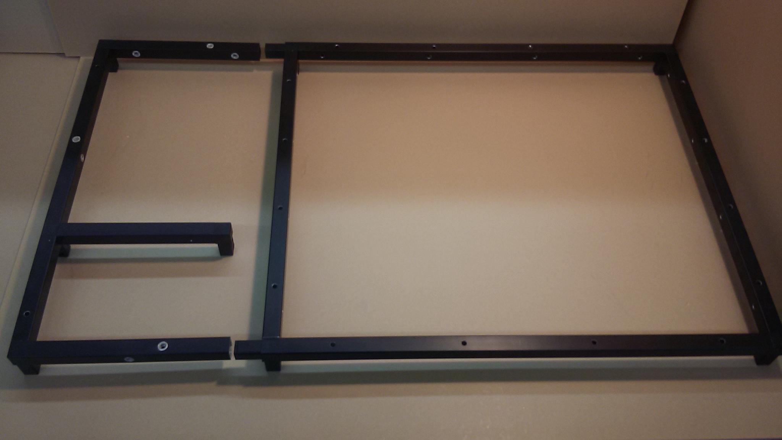
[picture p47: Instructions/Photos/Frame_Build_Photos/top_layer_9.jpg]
Final Top Frame

* *Wait! do not put the top half on. First, Assemble the Electronics Panel*

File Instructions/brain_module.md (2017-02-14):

## Assemble the Brain Module
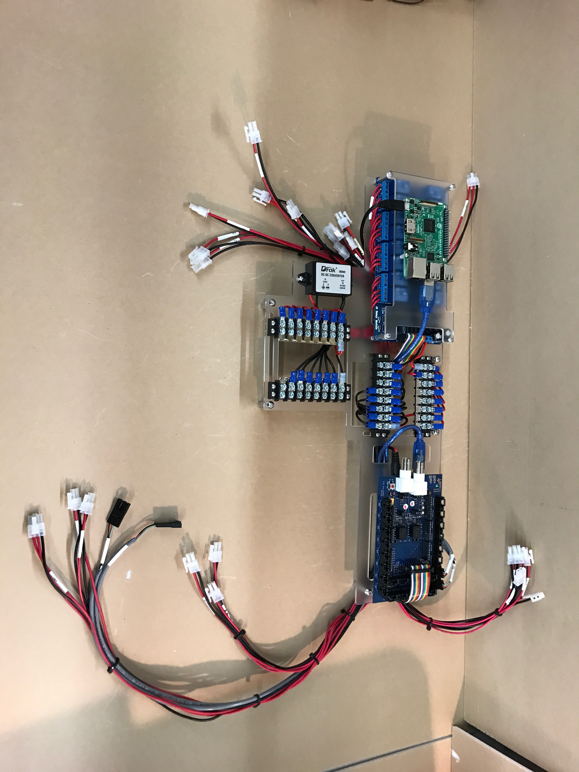
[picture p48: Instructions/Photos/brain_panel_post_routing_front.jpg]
brain_panel_post_routing_front


### Tools
 - Small Flathead Screwdriver
 - Medium Phillips Screwdriver
 - Standard Hex Driver Set
 - Wire Cutters

### Instructions
 1. Gather materials for this submodule. See BOM-Master's PFC2-MOD-0001 tab
 2. Peel off the protective covering on both sides of the **Brain Manifold Panel** & **Raspberry Pi Mounting Panel**
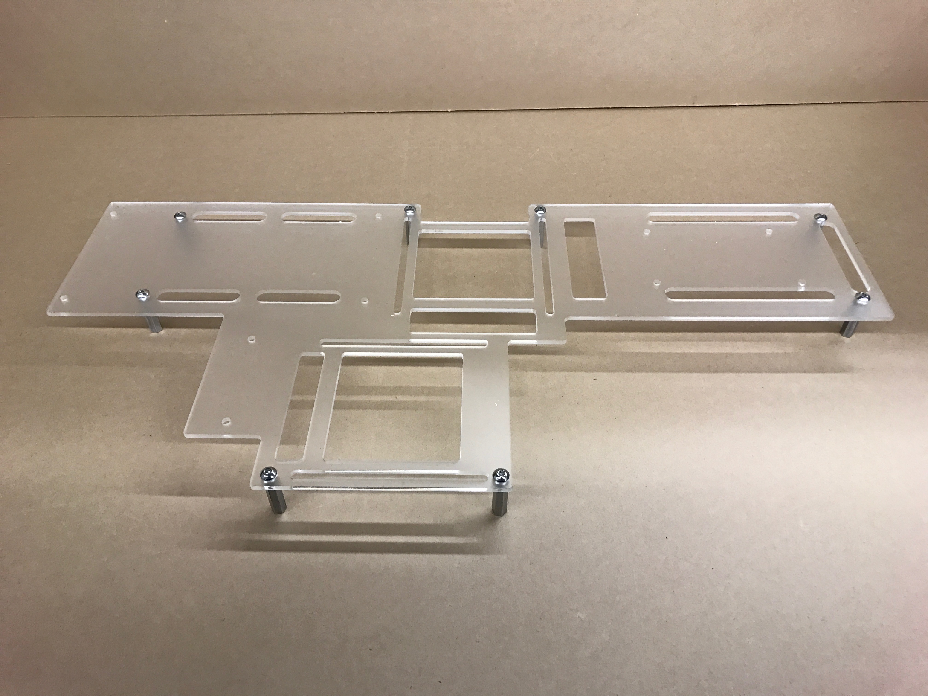
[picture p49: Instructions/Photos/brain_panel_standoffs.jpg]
brain_panel_standoffs
 3. Attach x8 of the **S-#08-32-100-STD-H-AL-FF (Bag 7)** (8-32 x 1" Aluminum Standoffs) to the Brain Manifold Panel with x8 of the **S-#08-32-050-BTN-S-SS (Bag 3)** (8-32 x 1/2" Button Head Screws) as shown in 
 4. Attach an **8-Pos Barrier Block Jumpers** (PWR-BUS-0002) to a single side of the **8-Pos Barrier Block** (PWR-BUS-0001). Attach the jumper to all x4 blocks.
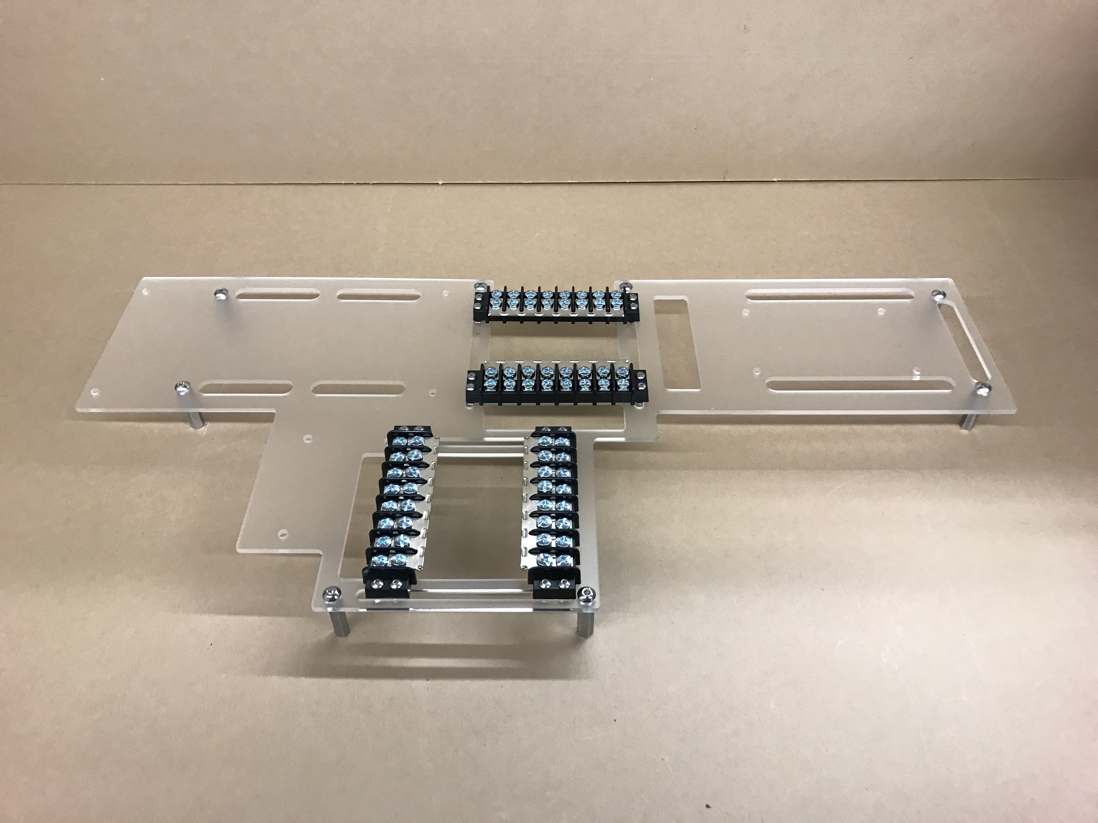
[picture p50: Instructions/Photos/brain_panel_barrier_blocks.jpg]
brain_panel_barrier_blocks
 5. Mount x4 of the **8-Pos Barrier Blocks** to the **Brain Manifold Panel** with x16 of the **S-#04-40-050-BTN-S-SS (Bag 11)** (4-40 x 1/2" Button Head Screws) and x16 of the **S-#04-40-094-NUT-H-SS (Bag 15)** (4-40 Nuts) as shown in 
 6. Mount the **16-Channel Relay Board** (ELC-REL-0001) to the **Brain Manifold Panel** with x4 of the **S-#04-40-025-STD-H-AL-MF (Bag 17)** (4-40 x 1/4" Body Aluminum Standoff 3/16" Length, Male-to-Female), x4 of the **S-#04-40-075-STD-H-AL-FF (Bag 16)** (4-40 x 3/4" Aluminum Standoff Female-to-Female), and x4 of the **S-#04-40-025-BTN-S-SS (Bag 13)** (4-40 x 1/4" Button Head Screws)
 7. Mount the **Raspberry Pi 3 Model B** (ELC-PRC-0002) to the **Raspberry Pi Mounting Plate** (STR-PNL-0015) with x4 of the **S-#04-40-125-BTN-S-SS (Bag 12)** (4-40 x 1/8" Button Head Screws), x4 of the **S-#04-40-025-STD-H-NY-FF (Bag 18)** (4-40 x 1/4" Nylon Standoffs), and x4 of the **S-#04-40-025-BTN-S-SS (Bag 13)** (4-40 x 1/4" Button Head Screw)
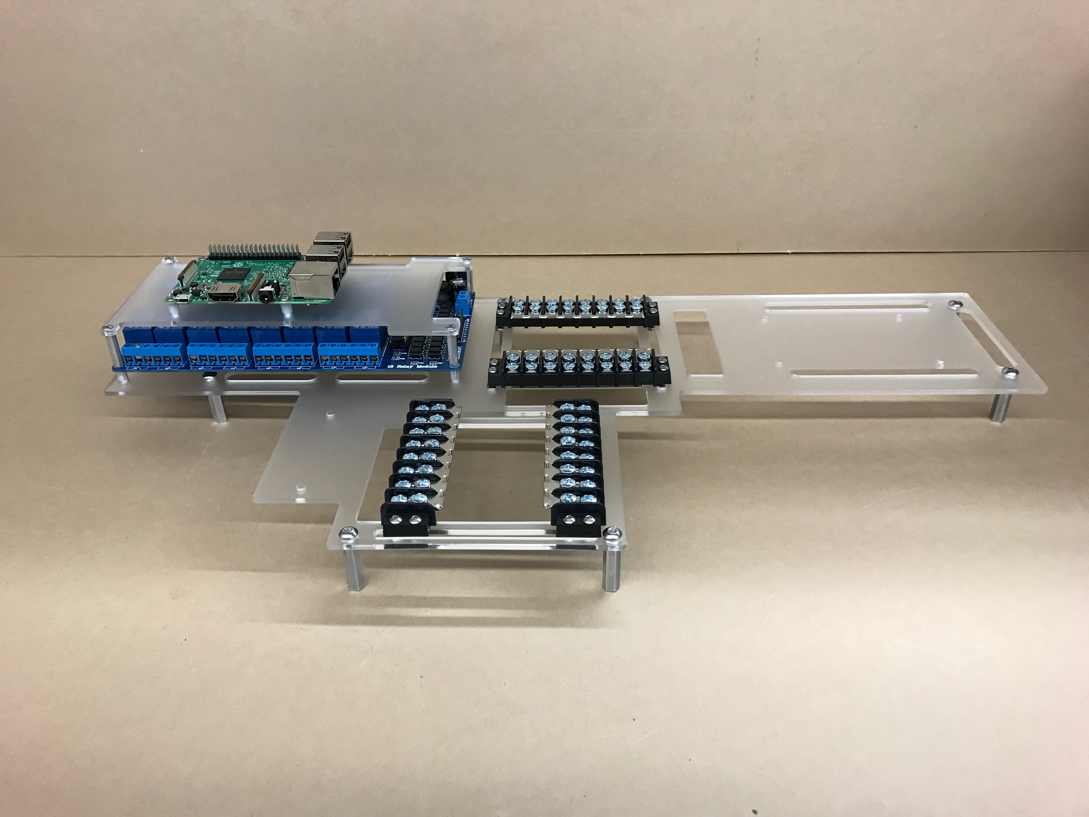
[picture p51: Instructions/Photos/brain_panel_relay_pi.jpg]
brain_panel_relay_pi
 8. Mount this panel on top of the **16-Channel Relay Board** with x4 of the **S-#04-40-025-BTN-S-SS (Bag 13)** (4-40 x 1/4" Button Head Screws). The assembly should now look like 
 9. Mount the **Arduino Mega** (ELC-PRC-0001) to the **Brain Manifold Panel** with x4 of the **S-#04-40-025-STD-H-NY-FF (Bag 18)** (4-40 x 1/4" Nylon Standoffs), x4 of the **S-#04-40-025-BTN-S-SS (Bag 13)** (4-40 x 1/4" Button Head Screws), and x4 of the **S-#04-40-125-BTN-S-SS (Bag 12)** (4-40 x 1/8" Button Head Screws)
 10. Use the Arduino's **USB A-to-B Cable** (WIR-CBL-0014)to connect the **Arduino Mega** to the **Raspberry Pi**. Route this cable on the under side of the panel.
 11. Stack the **OpenAg Signal Board v1.0** (ELC-PCB-0001) onto the **Arduino Mega**
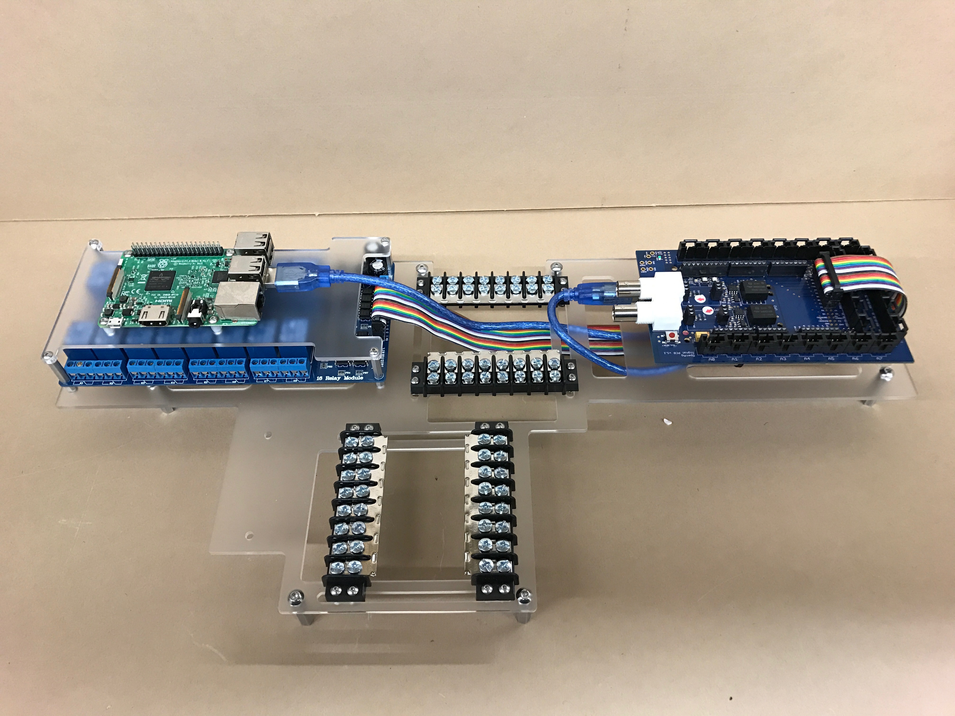
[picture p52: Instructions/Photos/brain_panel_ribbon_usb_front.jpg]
brain_panel_ribbon_usb_front
 12. Connect the row of 2x10 male header pins on the **Signal Board** to the row of 2x10 male header pins on the **16-Channel Relay Board** with the **20 Pos IDC Ribbon Cable 48cm, Rainbow Colored**. **IMPORTANT: The black wire on the outer edge of the ribbon cable should be in line with pins 44 & 45 on the signal board and 5V on the 16-channel relay board**. Be sure to check this with the picture below: 
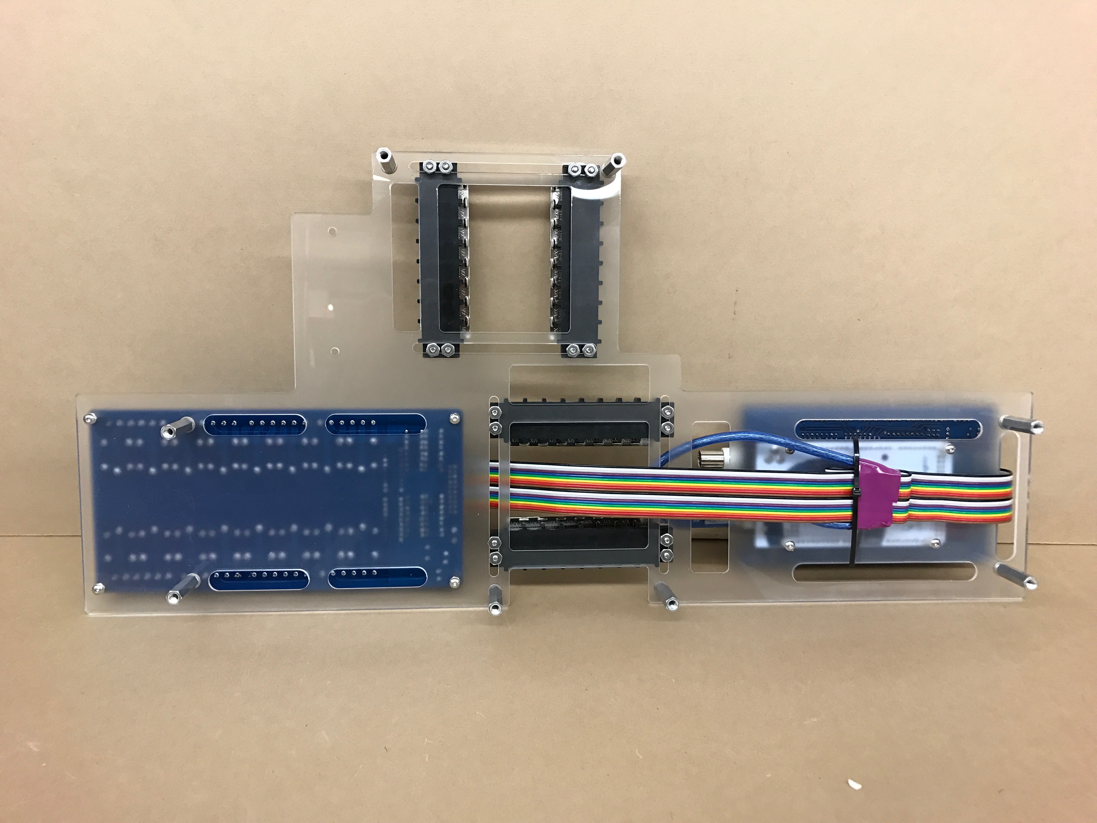
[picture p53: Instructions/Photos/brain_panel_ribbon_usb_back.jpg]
brain_panel_ribbon_usb_back
 13. Tape the **20 Pos IDC Ribbon Cable 48cm, Rainbow Colored** and the **USB A-to-B Cable** together and zip tie to the back side of the brain panel. See picture below: 
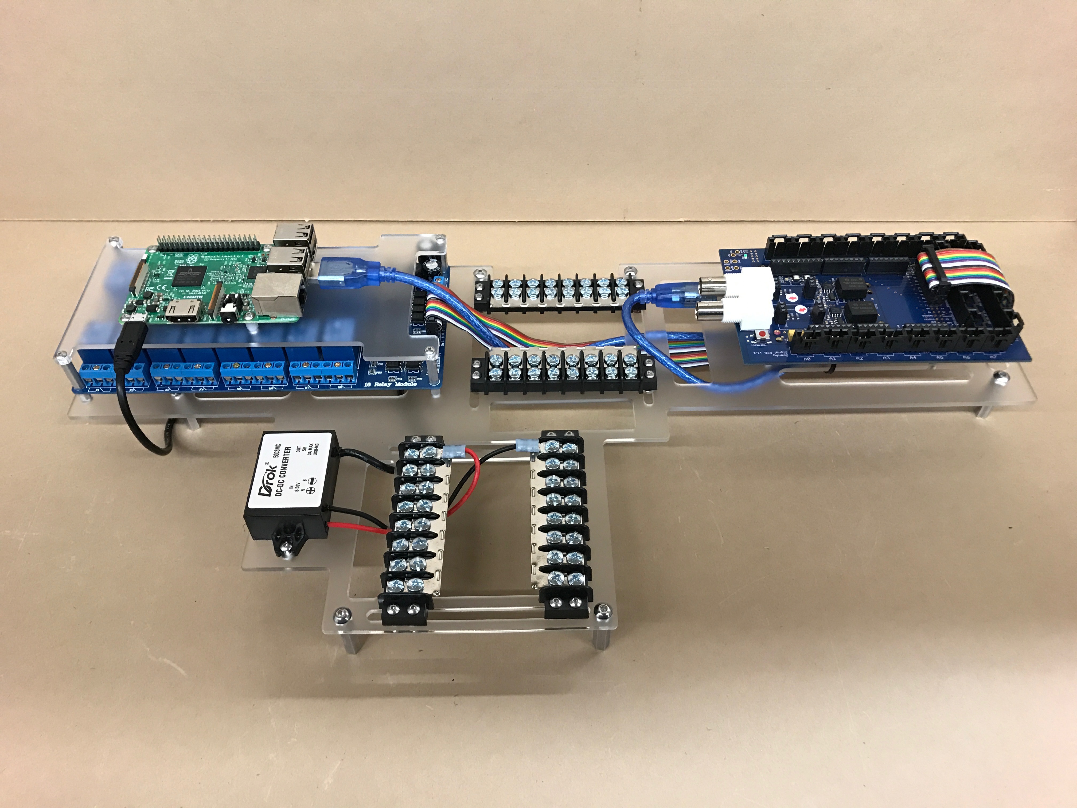
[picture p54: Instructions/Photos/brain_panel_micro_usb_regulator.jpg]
brain_panel_micro_usb_regulator
 14. Mount the **Connectorized Step-down Regulator with Micro USB Connector** (PWR-REG-CZD-0001) to the **Brain Manifold Panel** with x2 of the **S-#04-40-375-BTN-S-SS (Bag 14)** (4-40 x 3/8" Button Head Screws) and x2 of the **S-#04-40-094-NUT-H-SS (Bag 15)** (4-40 Nuts). Connect the red wire to 12V Bus 2, Terminal 16, the black wire to  GND Bus 2, Terminal 1, and the micro usb cable to the Raspberry Pi Micro USB Power Port. See image below: 
 15. Connect Relay Block VIN	to 12V Bus 1, Terminal 1 with **8 Stud 14-16 AWG Spade Terminal with 2" Red Wire Lead** (WIR-HAR-0001)
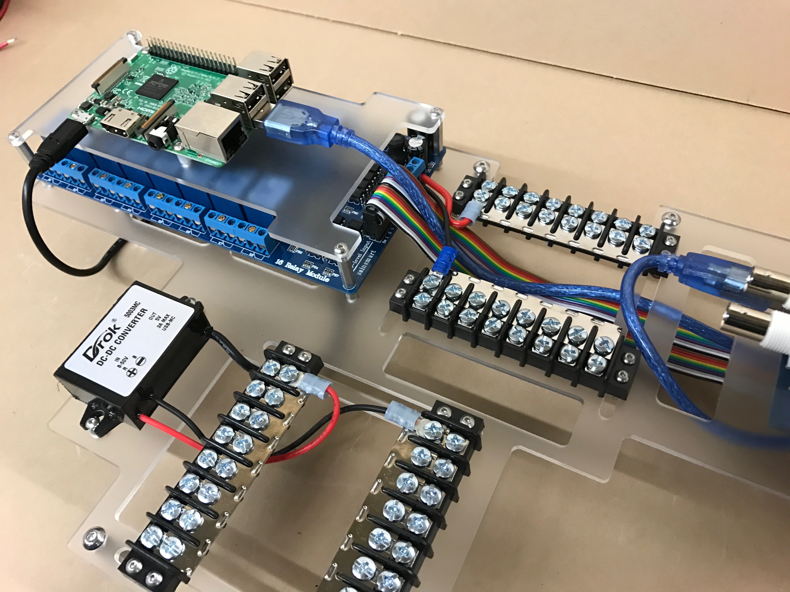
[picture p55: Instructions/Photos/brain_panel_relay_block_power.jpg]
brain_panel_relay_block_power
 16. Connect Relay Block GND to	GND Bus 1, Terminal 16 with **8 Stud 14-16 AWG Spade Terminal with 2.5" Black Wire Lead** (WIR-HAR-0002). See photo below: 
 17. Connect Relay Block COM from K2-8 to 12V Bus 2, Terminal 2-8 with x7 of the **8 Stud 14-16 AWG Spade Terminal with 10" Red Wire Lead** (WIR-HAR-0003). Use the Wire Cutter to trim the ends of the leads so they fit perfectly into the screw-down terminal. There should not be any exposed wire protruding from the terminal.
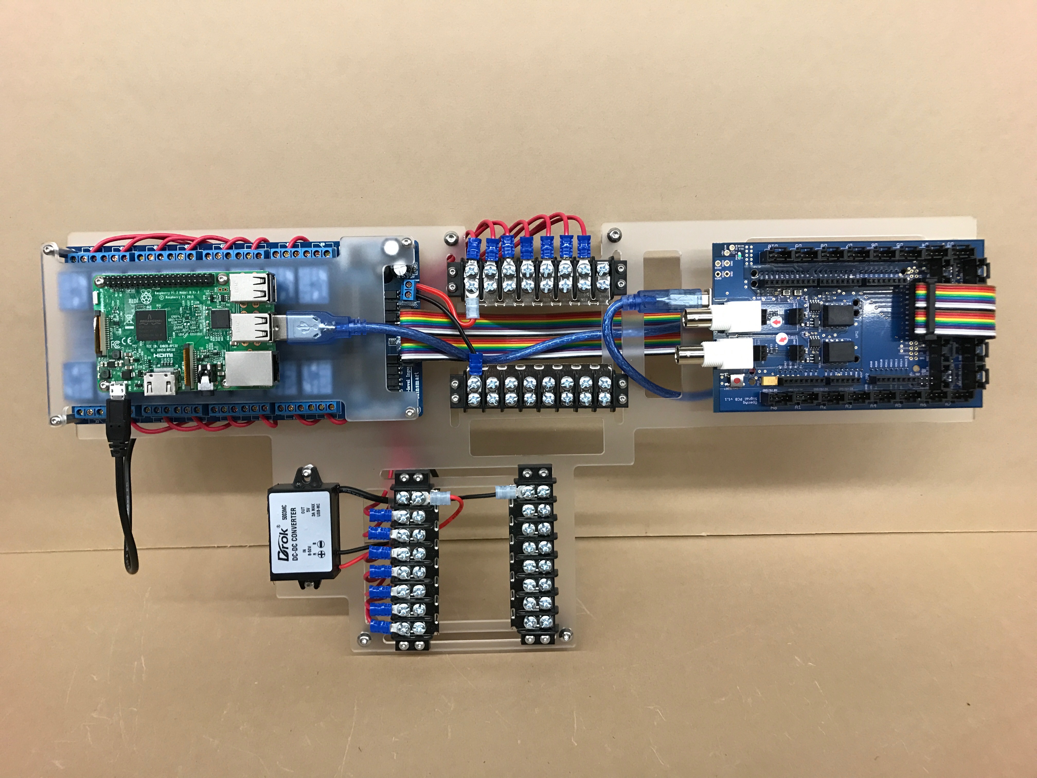
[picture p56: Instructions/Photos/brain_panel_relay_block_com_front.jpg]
brain_panel_relay_block_com_front
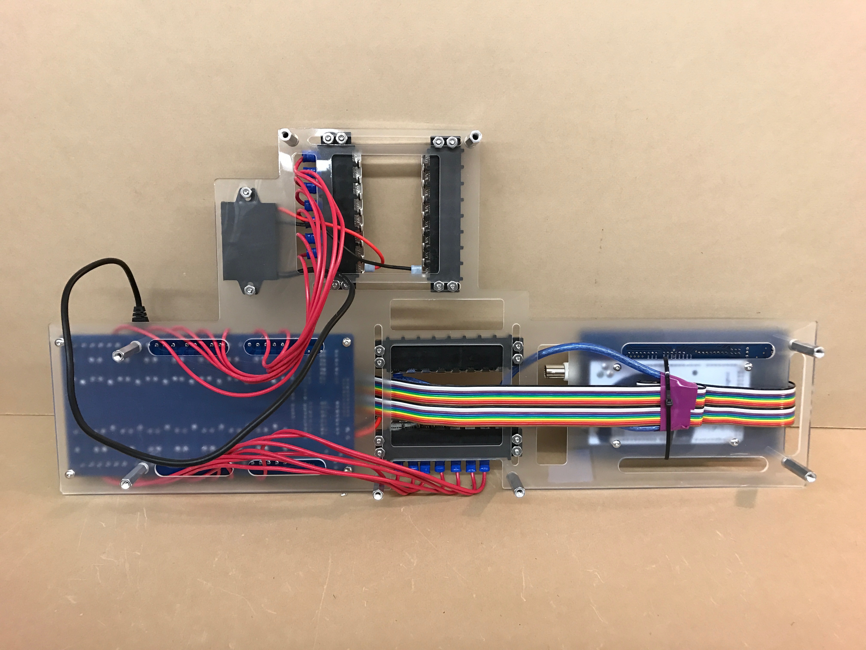
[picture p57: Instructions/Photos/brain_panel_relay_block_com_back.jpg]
brain_panel_relay_block_com_back
 18. Connect Relay Block COM from K10-16 to 12V Bus 1, Terminal 10-16 with x7 of the **8 Stud 14-16 AWG Spade Terminal with 10" Red Wire Lead** (WIR-HAR-0003). Use the Wire Cutter to trim the ends of the leads so they fit perfectly into the screw-down terminal. There should not be any exposed wire protruding from the terminal. See Photos below:  
 19. Connect **Molex JR 2-Pos Recepticle to 8 Stud 14-16 AWG Spade Terminals with "12V@1" Label, 10" Leads** (WIR-HAR-0005) red wire to 12V Bus 1, Terminal 2 and black wire to GND Bus 1, Terminal 15
 20. Connect **Molex JR 2-Pos Recepticle to 8 Stud 14-16 AWG Spade Terminals with "12V@2" Label, 10" Black Lead, 8" Red Lead** (WIR-HAR-0006) red wire to 12V Bus 2, Terminal 1 and black wire to GND Bus 2, Terminal 2
 21. Connect **Molex JR 2-Pos Recepticle-to-Recepticle with "12V@3" and "K1" Labels on 21" Red Leads with 15" Black Interconnect** (WIR-HAR-0007) "K1-COM" labelled red wire to K1-COM and the "K1-NO" labelled red wire to K1-NO on the **16-Channel Relay Board**
 22. Connect **Molex JR 2-Pos Recepticle-to-Recepticle with "12V@4" and "K9" Labels on 21" Red Leads with 15" Black Interconnect** (WIR-HAR-0036) "K9-COM" labelled red wire to K9-COM and the "K9-NO" labelled red wire to K9-NO on the **16-Channel Relay Board**
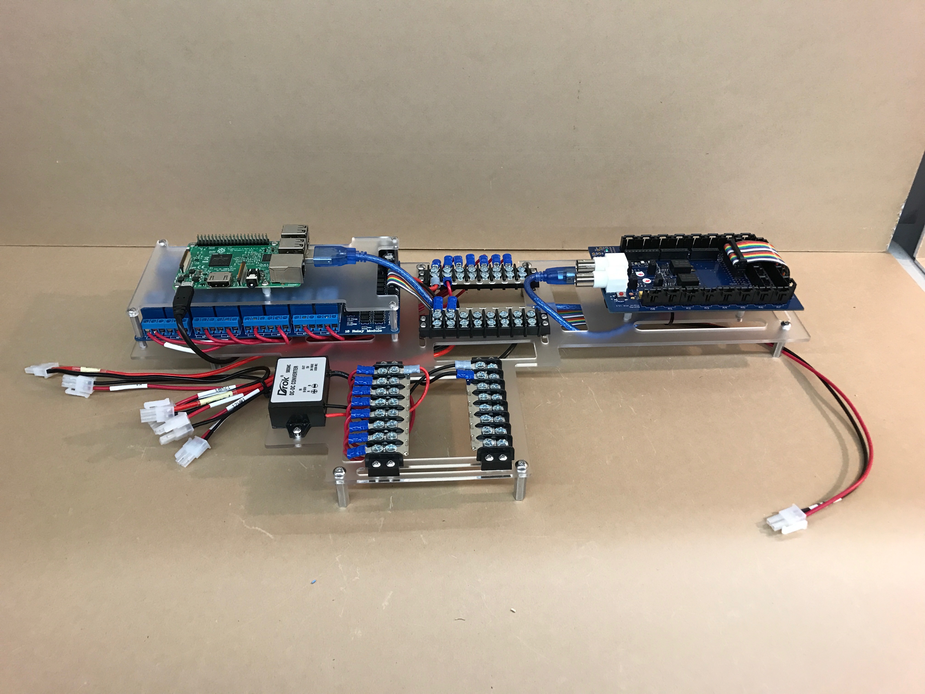
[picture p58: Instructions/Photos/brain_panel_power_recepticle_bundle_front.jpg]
brain_panel_power_recepticle_bundle_front
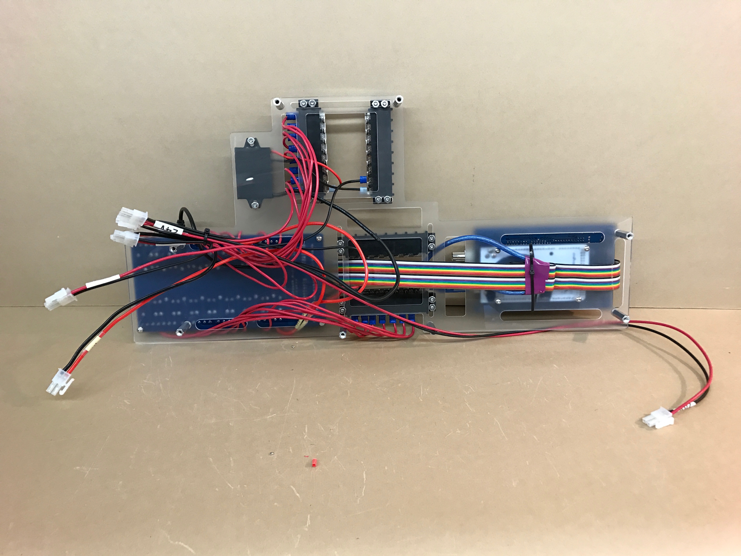
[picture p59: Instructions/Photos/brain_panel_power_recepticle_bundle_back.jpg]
brain_panel_power_recepticle_bundle_back
 23. Bundle together the 12V@1, 12V@2, 12V@3, 12V@4, along with one end of the **Molex JR 2-Pos Recepticle-to-Recepticle Cable with "24V" Label, 26"** (WIR-HAR-0004) and zip tie them together as shown in  
 24. Connect **Molex JR 2-Pos Recepticle with "K2" Label to 21" Black Lead with 8 Stud 14-16 AWG Spade Terminals, 24" Red Lead** (WIR-HAR-0008) black wire to	GND Bus 2, Terminal 3 and red wire to Relay Block K2-NO
 25. Connect **Molex JR 2-Pos Recepticle with "K3" Label to 21" Black Lead with 8 Stud 14-16 AWG Spade Terminals, 24" Red Lead** (WIR-HAR-0009) black wire to	GND Bus 2, Terminal 4 and red wire to Relay Block K3-NO
 26. Connect **Molex JR 2-Pos Recepticle with "K4" Label to 21" Black Lead with 8 Stud 14-16 AWG Spade Terminals, 24" Red Lead** (WIR-HAR-0010) black wire to	GND Bus 2, Terminal 5 and red wire to Relay Block K4-NO
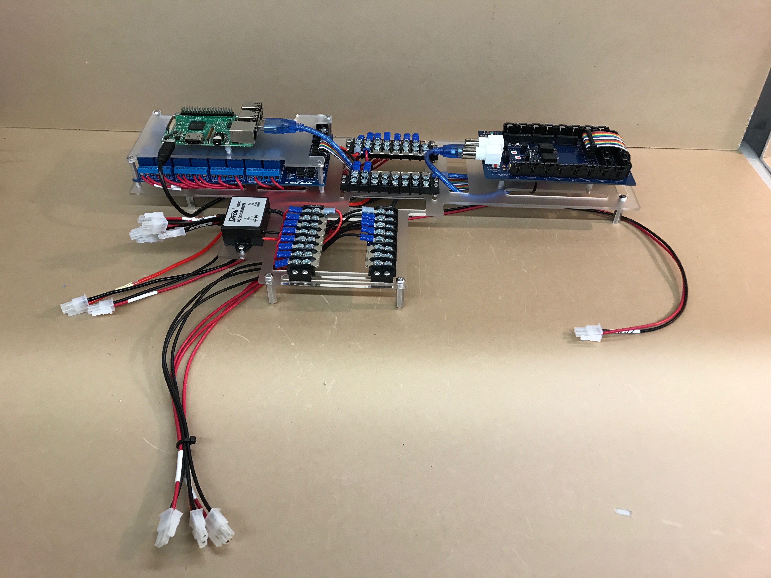
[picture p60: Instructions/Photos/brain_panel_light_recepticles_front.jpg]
brain_panel_light_recepticles_front
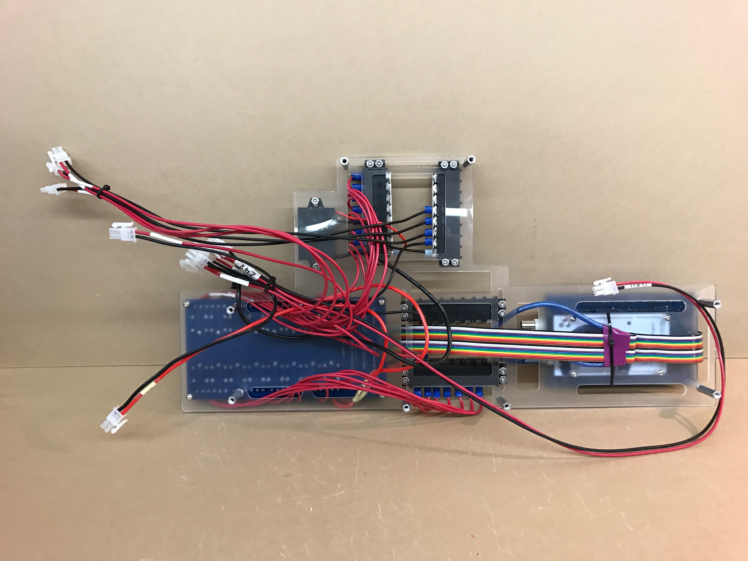
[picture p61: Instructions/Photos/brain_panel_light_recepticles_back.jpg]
brain_panel_light_recepticles_back
 27. Bundle together K2, K3, and K4 then zip tie them together near the end of the recepticle as shown:  
 28. Connect **Molex JR 2-Pos Recepticle with "K5" Label to 17" Black Lead with 8 Stud 14-16 AWG Spade Terminals, 18" Red Lead** (WIR-HAR-0011) black wire to	GND Bus 2, Terminal 6 and red wire to Relay Block K5-NO
 29. Bundle together K1, K5, and K9 such that they are staggered by a little more than a connectors length then zip tie them together.
 30.  Connect **Molex JR 2-Pos Recepticle with "K6" Label to 36" Black Lead with 8 Stud 14-16 AWG Spade Terminals, 42" Red Lead** (WIR-HAR-0012) black wire to	GND Bus 1, Terminal 6 and red wire to Relay Block K6-NO
 31.  Connect **Molex JR 2-Pos Recepticle with "K7" Label to 30" Black Lead with 8 Stud 14-16 AWG Spade Terminals, 36" Red Lead** (WIR-HAR-0013) black wire to	GND Bus 1, Terminal 7 and red wire to Relay Block K7-NO
 32. Connect **Molex JR 3-Pos Recepticles with "K8@1" and "K8@2" Labels, Spliced together with "K8-NC" and "K8-NO" labelled leads** (WIR-HAR-0014) K8@1 black wire to GND Bus 1, Terminal 8, K8@2 black wire to GND Bus 2, Terminal 7, red wire labelled "K8-NC" to Relay Block K8-NC and red wire labelled "K8-COM" to Relay Block K8-COM
 33. Connect **Molex SR 4-Pos Recepticle-to-Plug with "D3" Labels, 26"** (WIR-HAR-0022) to Signal Board D3
 34. Connect **Molex SR 4-Pos Recepticle-to-Plug with "D4" Labels, 26"** (WIR-HAR-0023) to Signal Board D4
 35. Bundle together K6, K7, K8@1, D3, and D4 then zip tie them together 8" away from the end connectors as shown below
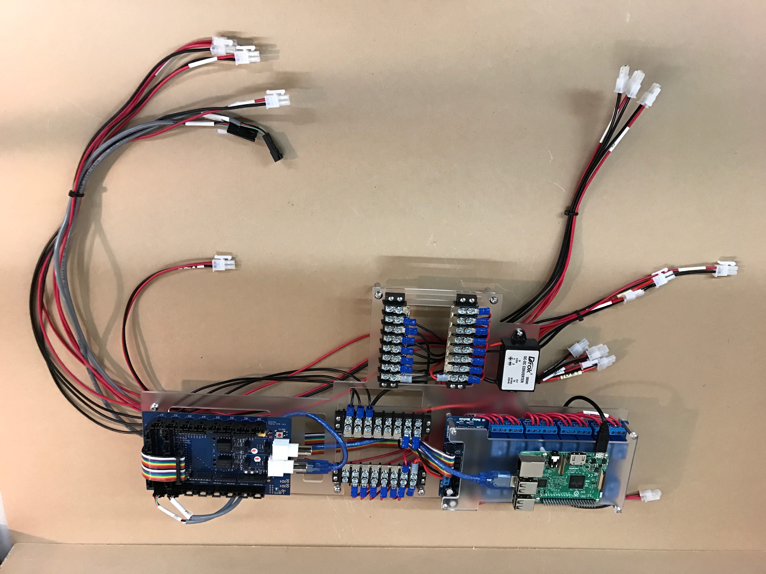
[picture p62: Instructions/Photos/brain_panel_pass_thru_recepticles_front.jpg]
brain_panel_pass_thru_recepticles_front
 
 brain_panel_pass_thru_recepticles_back
 36. Connect **Molex JR 2-Pos Recepticle with "K10" Label to 22" Black Lead with 8 Stud 14-16 AWG Spade Terminals, 29" Red Lead** (WIR-HAR-0015) black wire to GND Bus 1, Terminal 4 and red wire to K10-NO
 37. Connect **Molex JR 2-Pos Recepticle with "K11" Label to 22" Black Lead with 8 Stud 14-16 AWG Spade Terminals, 29" Red Lead** (WIR-HAR-0016) black wire to GND Bus 1, Terminal 5 and red wire to K11-NO
 38. Bundle together K10, K11, and 24V and zip tie together
 39. Connect **Molex JR 2-Pos Recepticle with "K12" Label to 19" Black Lead with 8 Stud 14-16 AWG Spade Terminals, 27" Red Lead** (WIR-HAR-0017) black wire to GND Bus 1, Terminal 10 and red wire to K12-NO
 40. Connect **Molex JR 2-Pos Recepticle with "K13" Label to 19" Black Lead with 8 Stud 14-16 AWG Spade Terminals, 27" Red Lead** (WIR-HAR-0018) black wire to GND Bus 1, Terminal 11 and red wire to K13-NO
 41. Connect **Molex JR 2-Pos Recepticle with "K14" Label to 19" Black Lead with 8 Stud 14-16 AWG Spade Terminals, 27" Red Lead** (WIR-HAR-0019) black wire to GND Bus 1, Terminal 12 and red wire to K14-NO
 42. Connect **Molex JR 2-Pos Recepticle with "K15" Label to 19" Black Lead with 8 Stud 14-16 AWG Spade Terminals, 27" Red Lead** (WIR-HAR-0020) black wire to GND Bus 1, Terminal 13 and red wire to K15-NO
 43. Connect **Molex JR 2-Pos Recepticle with "K16" Label to 19" Black Lead with 8 Stud 14-16 AWG Spade Terminals, 27" Red Lead** (WIR-HAR-0021) black wire to GND Bus 1, Terminal 14 and red wire to K16-NO
 44. Bundle together K12, K13, K14, K15, and K16 and zip tie them together.
 45. Connect **Inline Barrel Plug with Leads, Connectorized** (WIR-CBL-CZD-0001) black wire to GND Bus 1, Terminal 9, red wire to 12V Bus 1, Terminal 9, and the barrel plug to the **Arduino Mega** Barrel Jack. The assembly should now look something like this:
 brain_panel_pre_routing_front
 brain_panel_pre_routing_back
 46. Bundle the ratsnest on the back side into an orderly wire route by starting at the edges of the bundle and then moving inward. For example, bundle the all the red wires near the 12V bus that are close to each other. Do this for all the power bus bars. Then, move to the connectors on the other side of the wires and make sure the red and black wires coming into the them are of even lengths. Slowly tie the wires into the "main veins" and adjust as needed to make the routing look clean. It may be helpful to use place holder zip-ties in the process to help organize the clutter. Make sure the wires end up routed as they are in the photo below:
brain_panel_post_routing_front
brain_panel_post_routing_back

### Mounting the Brain Manifold
1. Before Mounting the Brain Manifold, Make sure to route the wire harness around the Standoffs as seen here: Wire Harness Routing
2. The Brain Manifold is mounted via x8 **S-#08-32-050-BTN-S-SS (Bag 3)** (8-32 x 050 button head) screws. Note the mounting position. Brain Manifold Mounting

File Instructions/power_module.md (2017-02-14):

##Assemble the Power Module
power_module_assembly_front

### Tools
 - Balldriver Set, Standard
 - Balldriver Set, Metric
 - Nutdriver Set, Standard
 - Nutdriver Set, Metric
 - Wire Cutters
 - Pliars
 - Phillips Head Screwdriver

### Instructions
 1. Gather all materials for this subassembly as shown: power_module_materials
 2. **PLEASE READ, THIS IS VERY IMPORTANT: Set the 12V power supply to either 115V or 230V depending on where you live. If you do not do this properly, this will damage the suppy and make it unusable.**
 3. Insert x2 of the **Glass Fuses** (ELC-FUS-0001) into the **Power Entry Module** (ELC-PEM-0001) as shown: power_module_power_entry_fuse
 4. Insert the **Fused Power Entry Module** and **Power Switch** (ELC-SWI-0001) into the **Large Power Supply Bracket** (STR-PNL-0002) as shown. **IMPORTANT: Make sure to have the correct orientation as it is very difficult to take them back out after they are inserted** power_module_inserted_switch_power_entry
 5. Mount the **Multifunction Programmable Relay Timer** (ELC-REL-0002) to one of the **Small Power Supply Brackets** (STR-PNL-0003) with x4 of the **S-#04-40-025-BTN-S-SS (Bag 13)** (4-40 x 0.25" Button Head Screws), x4 of the **S-#04-40-025-STD-H-AL-MF (Bag 17)** (4-40 x 0.25" Aluminum Standoff, Male-to-Female, 0.1875" Length), and x4 of the **S-#04-40-094-NUT-H-SS (Bag 15)** (4-40 Nuts) as shown: power_module_relay_mount
 6. Mount the **Small Power Supply Brackets** to the **Large Power Supply Bracket** with x4 of the **S-#08-32-025-BTN-S-SS (Bag 1)** (8-32 x 0.25" Button Head Screws) and x4 of the **S-#08-32-094-NUT-H-SS (Bag 6)** (8-32 Nuts) as shown: power_module_brackets
 7. Mount the **24V Power Supply** (PWR-SUP-0001) to the **Assembled Power Supply Brackets** with x2 of the **M-004-07-014-BTN-S-SS (Bag 29)** (M4 x 14mm Button Head Screws) and x2 of the **M-004-07-005-BTN-S-SS (Bag 28)** (M4 x 5mm Button Head Screws) as shown: power_module_24v
 8. Connect the **Power Entry Module Load** to the **Power Switch Pos 1A** and **Multifunction Relay COM** with **0.250" Female Quick Connect Terminal 10-12 AWG with 17" Black Lead and 3" Black Wire to 0.250" Female Quick Connect Terminal 14-16 AWG** (WIR-HAR-0026) as shown: power_module_load
 9. Connect **Power Switch Pos 2A**, **Power Switch Pos 3A**, and **Multifunction Relay NO** with **Double 0.250" Female Quick Connect Terminal 10-12 AWG with 17", 21", and 21" Black Leads with 2" Black Wire Connecting Terminals** (WIR-HAR-0027). Make sure the orientation has the two unconnected black wires of apporximately equal length. See below: power_module_switched_load_initial
 10. Connect **0.250" Female Quick Connect Terminal 10-12 AWG with Two 18" White Leads** (WIR-HAR-0024) to **Power Entry Module Neutral (N)**
 11. Connect **Double 0.250" Female Quick Connect Terminal 10-12 AWG to Two 19" Green Leads Connected by 4.5" Green Wire** (WIR-HAR-0025) to **Power Entry Module Ground** and **Power Switch Pos 6B**
 12. Connect **Molex SR 4-Pos Plug with "RPI GPIO 11/13/15/17" Label with Varried Length Leads** (WIR-HAR-0034) red wire to **Power Switch Pos 4B** and yellow wire to **Power Switch Pos 5B**. The connections to the power switch and power entry module should now look like: power_module_connected_power_entry_and_switch
 13. Bundle the wires connecting to the **Power Entry Module** and **Power Switch** and zip  tie them together at the bottom of the **Power Entry Module**
 14. Tape over the entire **Power Entry Module** and **Power Switch** with Electrical Tape as shown: power_module_taped_power_entry_and_switch
 15. Connect the green wires to the grounds on each power supply
 16. Connect the black wires to the loads (L) on each power supply
 17. Connect the whites to the normals (N) on each power supply
 18. Connect the wire harness labelled 24V to the 24V power supply (black to -V and red to +V)
 19. Connect the wire harnesses labelled 12V@1, 12V@2, 12V@3, 12V@4, and the individual red and black wire harnesses to the 12V power supply (be sure to only put up to 2 wires per terminal)
 20. Connect the white 24 AWG (the skinny one) wire into CH1 on the multifunction relay
 21. Make sure there is tape around the end of the yellow 24 AWG wire and tape it next to the multifunction relay.
 22. Bundle the wires together at the edges (all wires connecting to the 12V supply are one edge, all wires connecting to the 24V supply are another edge, the recepticles are another edge). The assembly should now look like this: power_module_pre_routing
 23. Bundle together the main vein of wires and zip tie together as shown: power_module_main_vein_inside power_module_main_vein_outside
 24. Close up the routing zone by mounting the 12V power supply to the power supply brackets. Use x8 **M-004-07-005-BTN-S-SS (Bag 28)** (M4 x 5mm Button Head Screws). The finished assembly should look like: power_module_assembly_front power_module_assembly_bottom

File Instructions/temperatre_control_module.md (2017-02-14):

## Assemble the Temperature Control Module
1. Collect components listed in **Sub Assembly BOM's** **Temperature control module** tab.
2. Thread x2 **ACT-FTG-0001** Barb Fittings into the **ACT-XNG-0001 EX120** radiator.
3. Mount the **CFM-A238-13-10** Fan to the fitting side of the radiator using x4 **S-#06-32-312-BTN-S-SS** 6-32 screws. Make sure to orient the fan with its wires facing the wire pass through corner.
4. Mount the Electric Heater to the otherside of the radiator using x2 **S-#06-32-312-BTN-S-SS** 6-32 screws.
5. Fasten x4 **S-#08-32-150-STD-H-AL-FF** 8-32 x 1.5" standoffs to the fan using x4 **S-#08-32-375-BTN-S-SS** screws.

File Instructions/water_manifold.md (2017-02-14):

## Assemble the Water Manifold
* *on each panel there are finernail sized rectangular cutouts. Use these & zipties to route wires.*
1. See **Sub-Assembly BOM's** **"Water Manifold"** tab for a complete list of parts.
2. Join the two plastic panels together with x3 **S-#08-32-050-BTN-S-SS (Bag 3)**, **S-#08-32-094-NUT-H-SS (Bag 6)**, & **S-#08-00-125-LBR-O-SS (Bag 32)** stainless steel L-brackets.
3. Fasten two more **S-#08-32-050-BTN-S-SS (Bag 3)**, **S-#08-32-094-NUT-H-SS (Bag 6)**, & **S-#08-00-125-LBR-O-SS (Bag 32)** L-Brackets facing the opposite direction in the shown holes: L-Brackets on the Manifold
4. Thread one **S-050-NN-019-NUT-O-PL (Bag 40)** plastic NPT locknut onto the pependicular outlet of **ACT-PMP-CZD-0001** Circulation pump, flat side outward.
5. Thread the **ACT-FLT-0001** filter onto the inlet of the pump, inline with the body.
6. Fit the Outlet of the pump through a hole in the vertical section so the filter inlet is away from the sensors. Thread the other **S-050-NN-019-NUT-O-PL (Bag 40)** plastic NPT locknut onto the outlet.
7. Thread another **S-#08-32-094-NUT-H-SS (Bag 6)** L-bracket in place similar to the shown picure, using th same fasteners. for the Water level sensors [PIC: Water manifold assembly]higher
8. Mount two **SEN-PRB-CZD-0003** water level sensors in the ports on the small **STR-PNL-0009** water level sensor mounts.
9. Hang this assembly by the L-bracket from step 7, using the same **S-#08-00-125-LBR-O-SS (Bag 32)** & **S-#08-32-050-BTN-S-SS (Bag 3)** fasteners.
10. Route the **SEN-PRB-CZD-0003** temperature sensor through the the a larger hole in the water manifold, then Secure to a small cutout on the vertical using a ziptie.Water Manifold Components Connected
11. The PH and EC Sensors simply drop in place through any appropriate circular cutout. Make Sure Not to leave the PH sensor out of liquid for extended periods of time.

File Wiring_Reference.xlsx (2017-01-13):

Assembly | Connect This | To That | With
Brain Module | Inline Barrel Jack Plug | Arduino | Itself
 | Inline Barrel Jack Black Wire | GND Bus 1, Terminal 9 | Itself
 | Inline Barrel Jack Red Wire | 12V Bus 1, Terminal 9 | Itself
 | Micro-USB Step Down Converter MicroUSB Cable | Raspberry Pi Micro-USB Port | Itself
 | Micro-USB Step Down Converter Black Wire | GND Bus 2, Terminal 1 | Itself
 | Micro-USB Step Down Converter Red Wire | 12V Bus 2, Terminal 16 | Itself
 | Arduino USB | Raspberry Pi USB | WIR-CBL-0014
 | Signal Board GPIO Pass Through Pins 26-44 | Relay Block GPIO Header Pins 5V, 1-15, GND | WIR-CBL-0013
 | Relay Block VIN | 12V Bus 1, Terminal 1 | WIR-HAR-0001
 | Relay Block GND | GND Bus 1, Terminal 16 | WIR-HAR-0002
 | Relay Block K2-COM | 12V Bus 2, Terminal 2 | WIR-HAR-0003
 | Relay Block K3-COM | 12V Bus 2, Terminal 3 | WIR-HAR-0003
 | Relay Block K4-COM | 12V Bus 2, Terminal 4 | WIR-HAR-0003
 | Relay Block K5-COM | 12V Bus 2, Terminal 5 | WIR-HAR-0003
 | Relay Block K6-COM | 12V Bus 2, Terminal 6 | WIR-HAR-0003
 | Relay Block K7-COM | 12V Bus 2, Terminal 7 | WIR-HAR-0003
 | Relay Block K8-COM | 12V Bus 2, Terminal 8 | WIR-HAR-0003
 | Relay Block K10-COM | 12V Bus 1, Terminal 10 | WIR-HAR-0003
 | Relay Block K11-COM | 12V Bus 1, Terminal 11 | WIR-HAR-0003
 | Relay Block K12-COM | 12V Bus 1, Terminal 12 | WIR-HAR-0003
 | Relay Block K13-COM | 12V Bus 1, Terminal 13 | WIR-HAR-0003
 | Relay Block K14-COM | 12V Bus 1, Terminal 14 | WIR-HAR-0003
 | Relay Block K15-COM | 12V Bus 1, Terminal 15 | WIR-HAR-0003
 | Relay Block K16-COM | 12V Bus 1, Terminal 16 | WIR-HAR-0003
 | 24V Recepticle Black Wire | 24V Plug Black Wire | WIR-HAR-0004
 | 24V Recepticle Red Wire | 24V Plug Red Wire
 | 12V@1 Recepticle Black Wire | GND Bus 1, Terminal 15 | WIR-HAR-0005
 | 12V@1 Red Wire | 12V Bus 1, Terminal 2
 | 12V@2 Recepticle Black Wire | GND Bus 2, Terminal 2 | WIR-HAR-0006
 | 12V@2 Recepticle Red Wire | 12V Bus 2, Terminal 1
 | K1 & 12V@3 Recepticle K1 Red Wire | Relay Block K1-COM | WIR-HAR-0007
 | K1 & 12V@3 Recepticle 12V Red Wire | Relay Block K1-NO
 | K9 & 12V@4 Recepticle K1 Red Wire | Relay Block K9-COM | WIR-HAR-0036
 | K9 & 12V@4 Recepticle 12V Red Wire | Relay Block K9-NO
 | K2 Recepticle Black Wire | GND Bus 2, Terminal 3 | WIR-HAR-0008
 | K2 Recepticle Red Wire | Relay Block K2-NO
 | K3 Recepticle Black Wire | GND Bus 2, Terminal 4 | WIR-HAR-0009
 | K3 Recepticle Red Wire | Relay Block K3-NO
 | K4 Recepticle Black Wire | GND Bus 2, Terminal 5 | WIR-HAR-0010
 | K4 Recepticle Red Wire | Relay Block K4-NO
 | K5 Recepticle Black Wire | GND Bus 2, Terminal 6 | WIR-HAR-0011
 | K5 Recepticle Red Wire | Relay Block K5-NO
 | K6 Recepticle Black Wire | GND Bus 1, Terminal 6 | WIR-HAR-0012
 | K6 Recepticle Red Wire | Relay Block K6-NO
 | K7 Recepticle Black Wire | GND Bus 1, Terminal 7 | WIR-HAR-0013
 | K7 Recepticle Red Wire | Relay Block K7-NO
 | K8@1 Recepticle Black Wire | GND Bus 1, Terminal 8 | WIR-HAR-0014
 | K8@1 Recepticle Center Red Wire | Relay Block K8-NO
 | K8@1 Recepticle Outer Red Wire | Relay Block K8-NC
 | K8@2 Recepticle Black Wire | GND Bus 2 Terminal 7
 | K8@2 Recepticle Center Red Wire | Relay Block K8-NO
 | K8@2 Recepticle Outer Red Wire | Relay Block K8-NC
 | K10 Recepticle Black Wire | GND Bus 1 Terminal 4 | WIR-HAR-0015
 | K10 Recepticle Black Wire | Relay Block K10-NO
 | K11 Recepticle Black Wire | GND Bus 1 Terminal 5 | WIR-HAR-0016
 | K11 Recepticle Red Wire | Relay Block K11-NO
 | K12 Recepticle Black Wire | Relay Block K12-NO | WIR-HAR-0017
 | K12 Recepticle Red Wire | GND Bus 1, Terminal 10
 | K13 Recepticle Black Wire | Relay Block K13-NO | WIR-HAR-0018
 | K13 Recepticle Red Wire | GND Bus 1, Terminal 11
 | K14 Recepticle Black Wire | Relay Block K14-NO | WIR-HAR-0019
 | K14 Recepticle Red Wire | GND Bus 1, Terminal 12
 | K15 Recepticle Black Wire | Relay Block K15-NO | WIR-HAR-0020
 | K15 Recepticle Red Wire | GND Bus 1, Terminal 13
 | K16 Recepticle Black Wire | Relay Block K16-NO | WIR-HAR-0021
 | K16 Recepticle Red Wire | GND Bus 1, Terminal 14
 | D3 Recepticle | Signal Board D3 | WIR-HAR-0022
 | D4 Recepticle | Signal Board D4 | WIR-HAR-0023
Power Module | Power Entry Module Neutral | 12V Power Supply NEUTRAL | WIR-HAR-0024
 |  | 24V Power Supply NEUTRAL
 | Power Entry Module GND | 12V Power Supply GND | WIR-HAR-0025
 |  | 24V Power Supply GND
 |  | Power Switch Pos 4B
 | Power Entry Module Load | Power Switch Pos 1A | WIR-HAR-0026
 |  | Delay Relay COM
 | Switched Load | Power Switch Pos 2A | WIR-HAR-0027
 |  | Power Switch Pos 3A
 |  | 12V Power Supply LOAD
 |  | 24V Power Supply LOAD
 |  | Delay Relay NO
 | Delay Relay DC- | 12V Power Supply -V, Pos 4 | WIR-HAR-0028
 | Delay Relay DC+ | 12V Power Supply +V, Pos 7 | WIR-HAR-0029
 | 24V Plug Black Wire | 24V Power Supply -V, Pos 4 | WIR-HAR-0030
 | 24V Plug Red Wire | 24V Power Supply +V, Pos 7
 | 12V@1 Plug Black Wire | 12V Power Supply -V, Pos 5 | WIR-HAR-0031
 | 12V@1 Plug Red Wire | 12V Power Supply +V, Pos 8
 | 12V@2 Plug Black Wire | 12V Power Supply -V, Pos 6 | WIR-HAR-0032
 | 12V@2 Plug Red Wire | 12V Power Supply +V, Pos 9
 | 12V@3 Plug Black Wire | 12V Power Supply -V, Pos 6 | WIR-HAR-0033
 | 12V@3 Plug Red Wire | 12V Power Supply +V, Pos 9
 | 12V@4 Plug Black Wire | 12V Power Supply -V, Pos 7 | WIR-HAR-0037
 | 12V@4 Plug Red Wire | 12V Power Supply +V, Pos 10
 | Delay Relay CH1 | Raspberry Pi GPIO 11/13/15/17 | WIR-HAR-0034
 | Power Switch Pos 5B
 | Power Switch Pos 6B
Sensors | Low Level Sensor Plug | D3 Recepticle | Itself
 | High Level Sensor Plug | D4 Recepticle | Itself
 | Water Temperature Sensor Plug | Signal Board D5 | Itself
 | pH Sensor Probe | Signal Board Atlas Port (w/ corresponding pH circuit) | Itself
 | EC Sensor Probe | Signal Board Atlas Port (w/ corresponding EC circuit) | Itself
 | CO2 Sensor | Signal Board I2C_3 | WIR-HAR-0035
 | Temperature & Humidity Sensor | Signal Board I2C_1 | Itself
Actuators | Heater Plug | K1 Recepticle | Itself
 | White Light Plug | K2 Recepticle | Itself
 | Blue Light Plug | K3 Recepticle | Itself
 | Red Light Plug | K4 Recepticle | Itself
 | Circulation Fan Plug | K5 Recepticle | Itself
 | Aeration Pump Plug | K6 Recepticle | Itself
 | Circulation Pump | K7 Recepticle | Itself
 | Air Flush Exhaust Plug | K8@1 Recepticle | Itself
 | Air Flush Intake Plug | K8@2 Recepticle | Itself
 | Pump 5 (Bottom Right) Plug | K12 Recepticle | Itself
 | Pump 4 (Bottom Left) Plug | K13 Recepticle | Itself
 | Pump 3 (Center) Plug | K14 Recepticle | Itself
 | Pump 2 (Top Right) Plug | K15 Recepticle | Itself
 | Pump 1 (Top Left) Plug | K16 Recepticle | Itself
Chiller Module | Chiller Pump & LED Plug | K10 Recepticle | Itself
 | Chiller Fan Plug | K11 Recepticle | Itself
 | Chiller Driver Power Plug | 24V Recepticle | Itself
 | Chiller Driver Signal Plug 1 (w/3 contacts) | Pulse Generator | Itself - YEL/BLK contact go to GND in pulse generator
 | Chiller Driver Signal Plug 2 (w/2 contacts) | Signal Board D10 | Itself

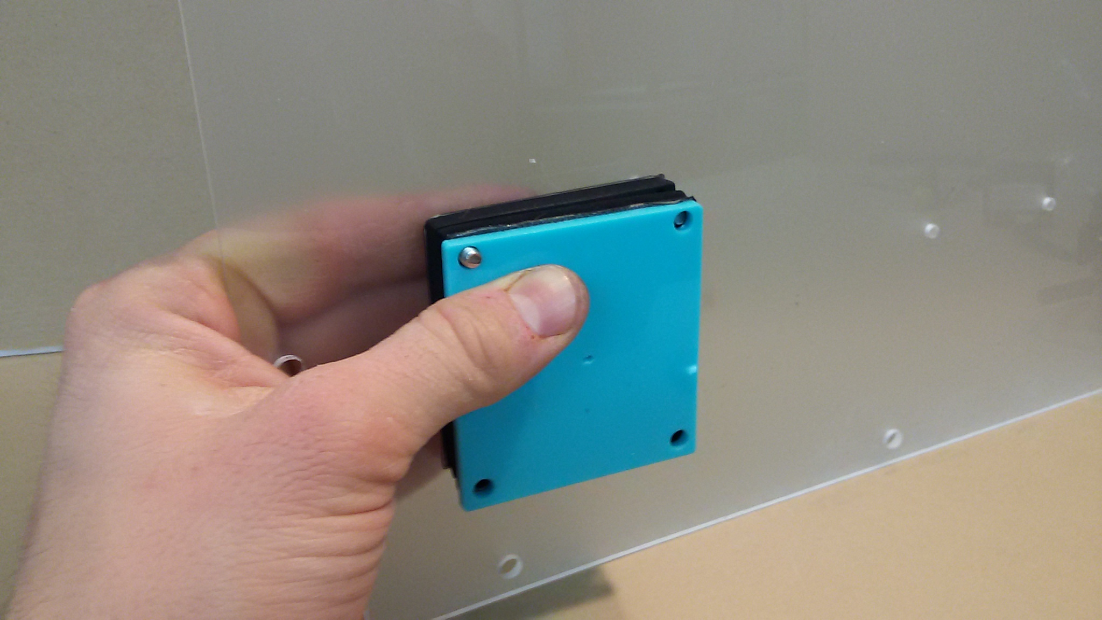
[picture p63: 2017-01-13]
Instructions/Photos/Inner_Side_Panel/Wire_Seals/inner_side_panel_8.jpg

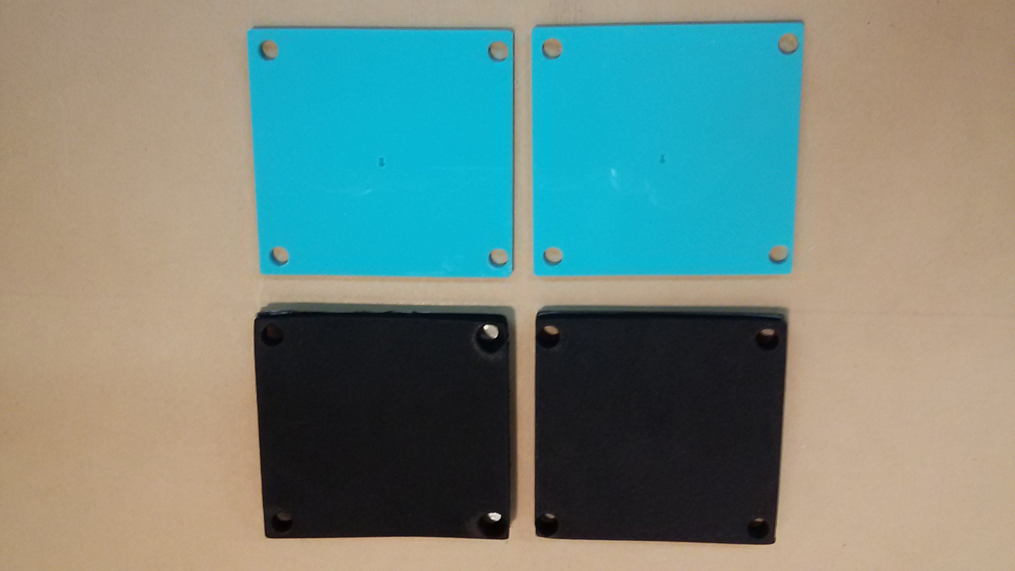
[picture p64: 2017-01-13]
Instructions/Photos/Inner_Side_Panel/Wire_Seals/wire_sealing.jpg

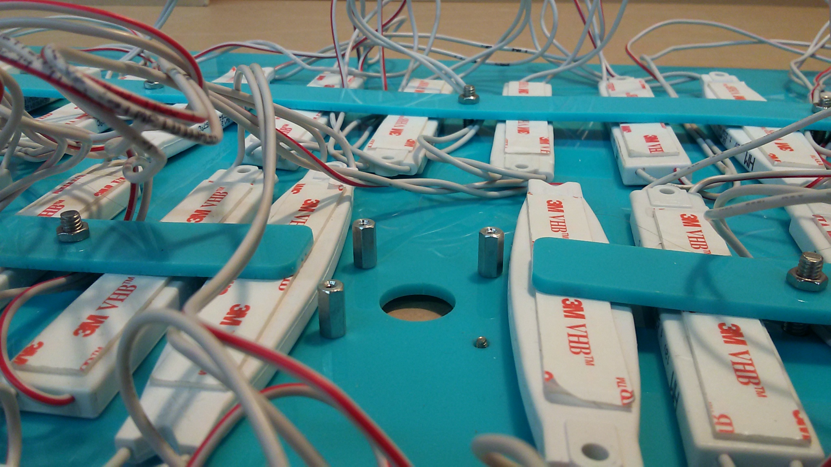
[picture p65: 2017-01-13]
Instructions/Photos/Light_Panel/camera_1.jpg

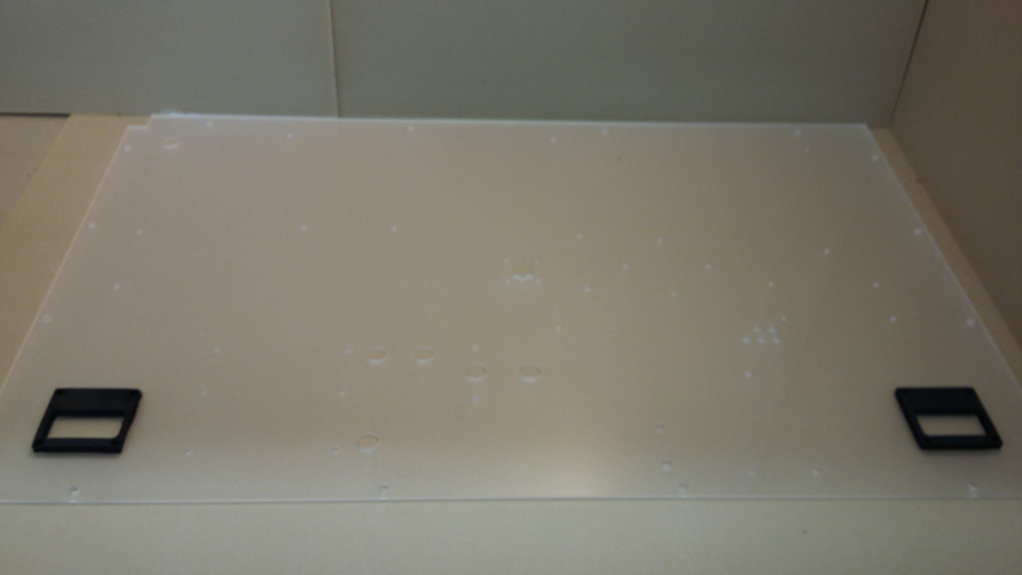
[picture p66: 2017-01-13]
Instructions/Photos/Inner_Side_Panel/Wire_Seals/inner_side_panel_3.jpg

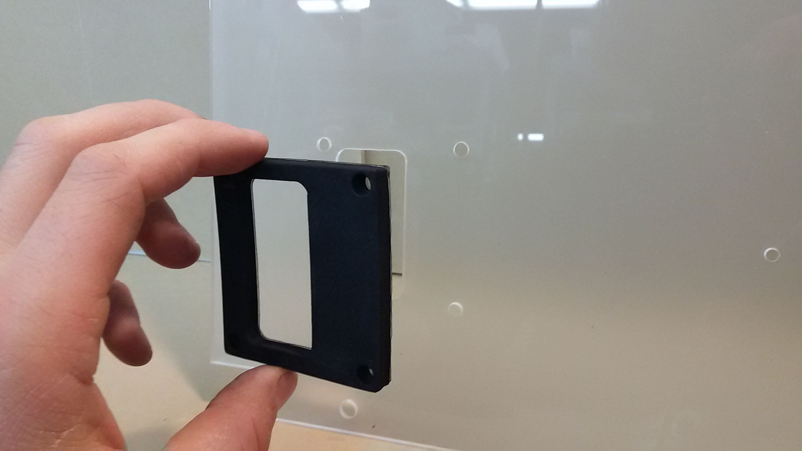
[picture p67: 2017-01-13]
Instructions/Photos/Inner_Side_Panel/Wire_Seals/wire_sealing_7.jpg

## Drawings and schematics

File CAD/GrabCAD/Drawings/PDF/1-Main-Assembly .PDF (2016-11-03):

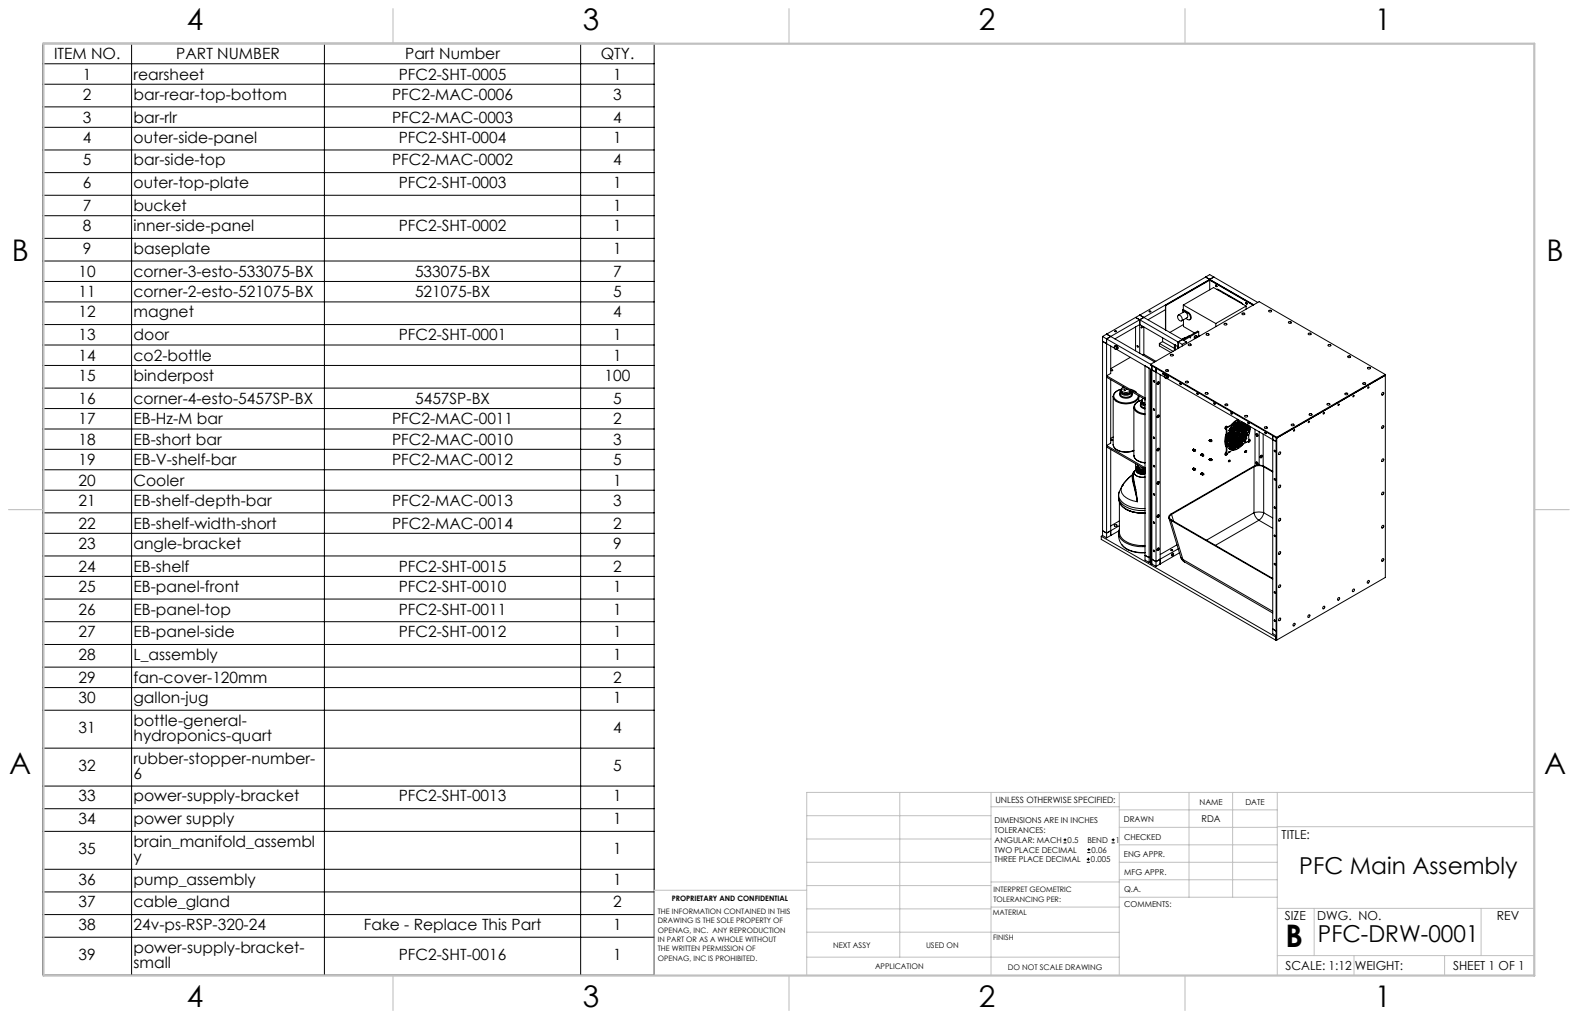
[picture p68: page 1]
power supply; TWO PLACE DECIMAL

ITEM NO. | PART NUMBER | Part Number | QTY.
1 | rearsheet | PFC2-SHT-0005 | 1
2 | bar-rear-top-bottom | PFC2-MAC-0006 | 3
3 | bar-rlr | PFC2-MAC-0003 | 4
4 | outer-side-panel | PFC2-SHT-0004 | 1
5 | bar-side-top | PFC2-MAC-0002 | 4
6 | outer-top-plate | PFC2-SHT-0003 | 1
7 | bucket | | 1
8 | inner-side-panel | PFC2-SHT-0002 | 1
9 | baseplate | | 1
10 | corner-3-esto-533075-BX | 533075-BX | 7
11 | corner-2-esto-521075-BX | 521075-BX | 5
12 | magnet | | 4
13 | door | PFC2-SHT-0001 | 1
14 | co2-bottle | | 1
15 | binderpost | | 100
16 | corner-4-esto-5457SP-BX | 5457SP-BX | 5
17 | EB-Hz-M bar | PFC2-MAC-0011 | 2
18 | EB-short bar | PFC2-MAC-0010 | 3
19 | EB-V-shelf-bar | PFC2-MAC-0012 | 5
20 | Cooler | | 1
21 | EB-shelf-depth-bar | PFC2-MAC-0013 | 3
22 | EB-shelf-width-short | PFC2-MAC-0014 | 2
23 | angle-bracket | | 9
24 | EB-shelf | PFC2-SHT-0015 | 2
25 | EB-panel-front | PFC2-SHT-0010 | 1
26 | EB-panel-top | PFC2-SHT-0011 | 1
27 | EB-panel-side | PFC2-SHT-0012 | 1
28 | L_assembly | | 1
29 | fan-cover-120mm | | 2
30 | gallon-jug | | 1
31 | bottle-general-hydroponics-quart | | 4
32 | rubber-stopper-number-6 | | 5
33 | power-supply-bracket | PFC2-SHT-0013 | 1

UNLESS OTHERWISE SPECIFIED: | NAME | DATE

DIMENSIONS ARE IN INCHES
TOLERANCES:
ANGULAR: MACH 0.5 BEND 1
THREE PLACE DECIMAL 0.005

35 | brain_manifold_assembl y | | 1
36 | pump_assembly | | 1
37 | cable_gland | | 2 | PROPRIETARY AND CONFIDENTIAL THE INFORMATION CONTAINED IN THIS DRAWING IS THE SOLE PROPERTY OF OPENAG, INC. ANY REPRODUCTION IN PART OR AS A WHOLE WITHOUT THE WRITTEN PERMISSION OF OPENAG, INC IS PROHIBITED.
38 | 24v-ps-RSP-320-24 | Fake - Replace This Part | 1
39 | power-supply-bracket-small | PFC2-SHT-0016 | 1

CHECKED | | TITLE: PFC Main Assembly

ENG APPR.
MFG APPR.

INTERPRET GEOMETRIC TOLERANCING PER: | Q.A.
MATERIAL | | SIZE B | DWG. NO. PFC-DRW-0001 | REV

NEXT ASSY | USED ON | FINISH

APPLICATION | DO NOT SCALE DRAWING | | SCALE: 1:12 WEIGHT: | | SHEET 1 OF 1

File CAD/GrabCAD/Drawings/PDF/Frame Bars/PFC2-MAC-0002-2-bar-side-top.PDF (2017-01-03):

4 | 3 | 2 | 1

# NOTES:

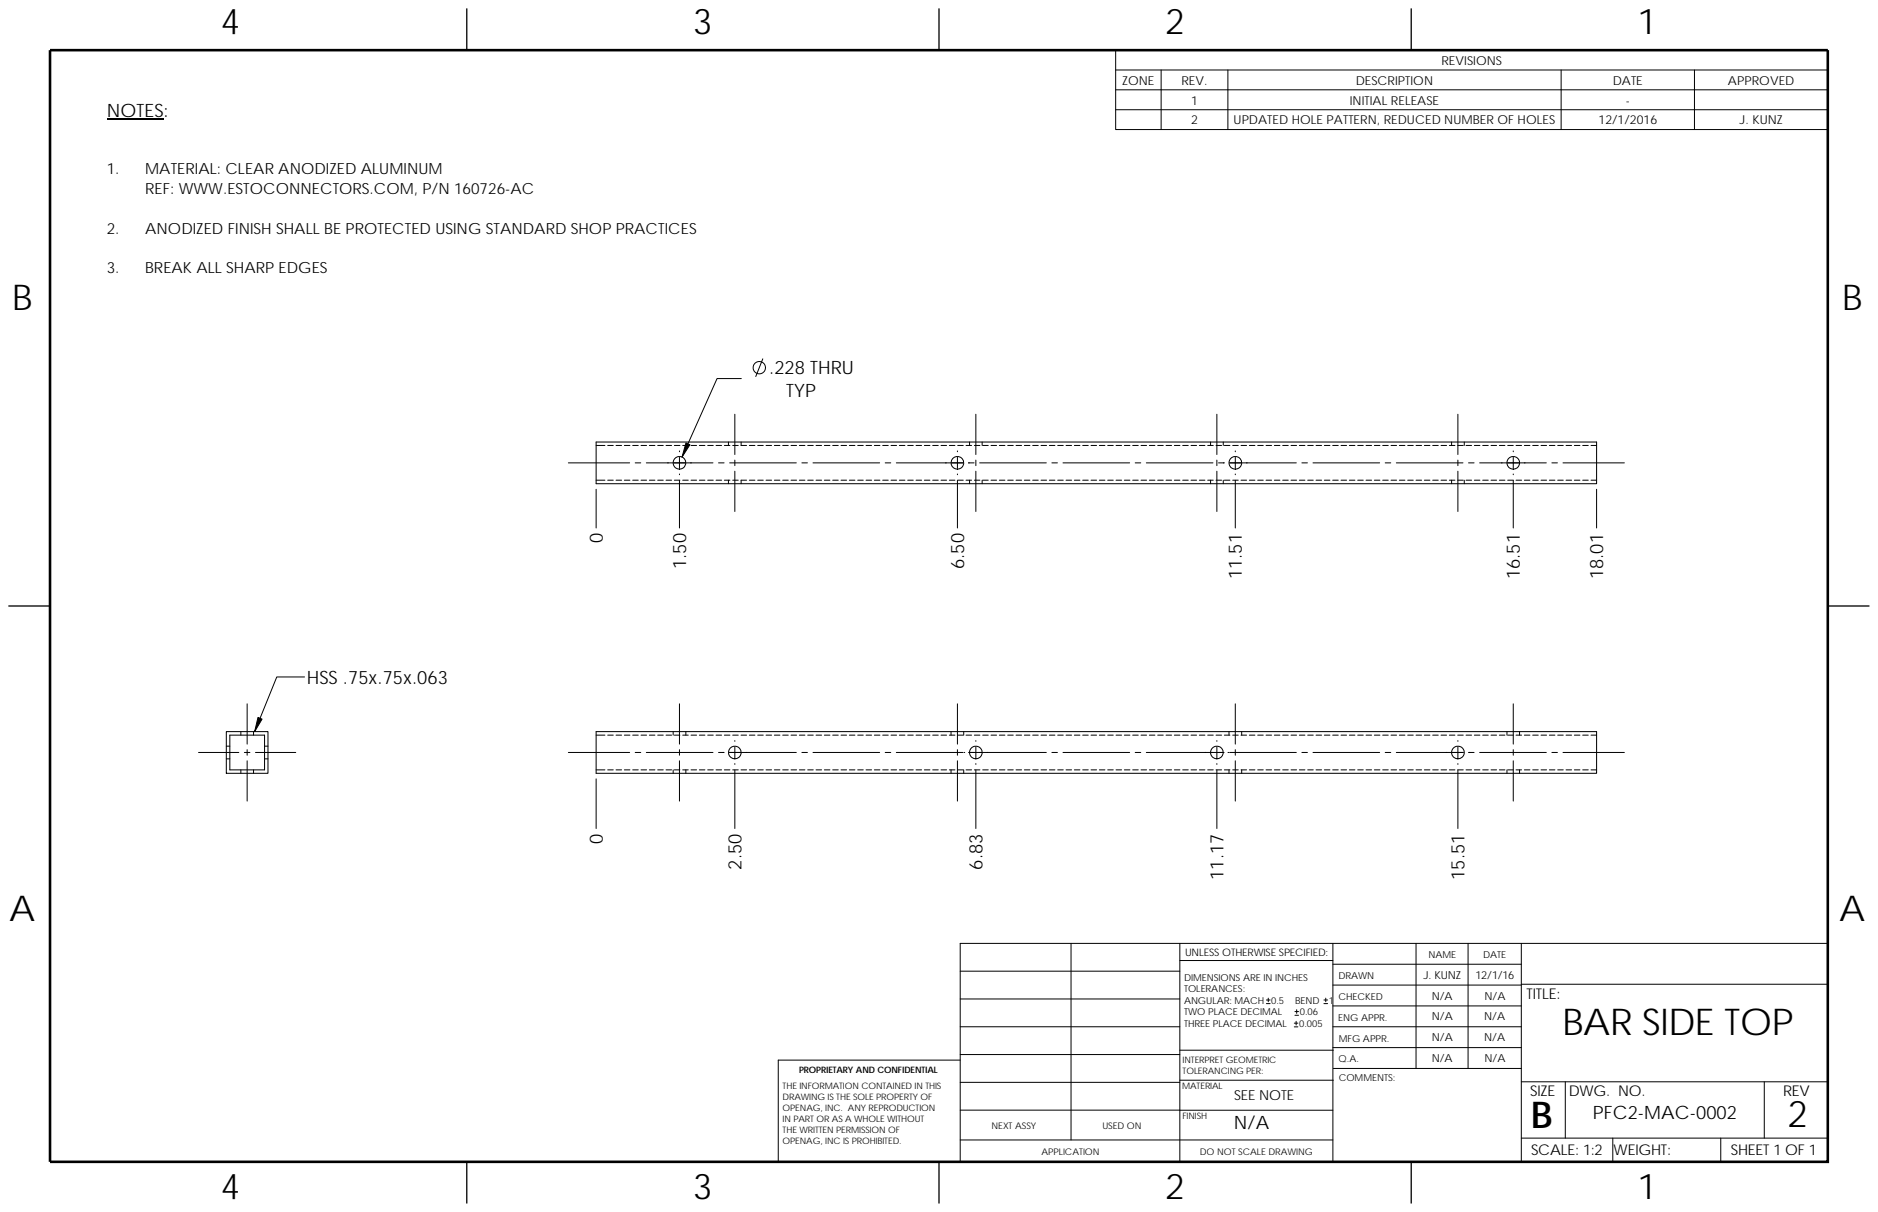
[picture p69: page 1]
COMMENTS:; REVISIONS; ZONE; REV.; DESCRIPTION; DATE; APPROVED; INITIAL RELEASE; UPDATED HOLE PATTERN, REDUCED NUMBER OF HOLES; J. KUNZ; HSS .75x.75x.063; .228 THRU TYP

1. MATERIAL: CLEAR ANODIZED ALUMINUM
REF: WWW.ESTOCONNECTORS.COM, P/N 160726-AC

2. ANODIZED FINISH SHALL BE PROTECTED USING STANDARD SHOP PRACTICES

3. BREAK ALL SHARP EDGES

UNLESS OTHERWISE SPECIFIED: | | NAME | DATE
DIMENSIONS ARE IN INCHES TOLERANCES: ANGULAR: MACH 0.5 BEND 1 TWO PLACE DECIMAL 0.06 THREE PLACE DECIMAL 0.005 | DRAWN | J. KUNZ | 12/1/16

CHECKED | N/A | N/A | TITLE: BAR SIDE TOP
ENG APPR. | N/A | N/A
MFG APPR. | N/A | N/A

INTERPRET GEOMETRIC TOLERANCING PER: | Q.A. | N/A | N/A
MATERIAL SEE NOTE N/A | | SIZE B | DWG. NO. PFC2-MAC-0002 | REV 2

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

NEXT ASSY | USED ON | FINISH
APPLICATION | DO NOT SCALE DRAWING | | SCALE: 1:2 | WEIGHT: | SHEET 1 OF 1

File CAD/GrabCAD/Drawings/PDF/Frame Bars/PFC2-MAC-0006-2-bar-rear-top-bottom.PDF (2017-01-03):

## REVISIONS

ZONE | REV. | DESCRIPTION | DATE | APPROVED

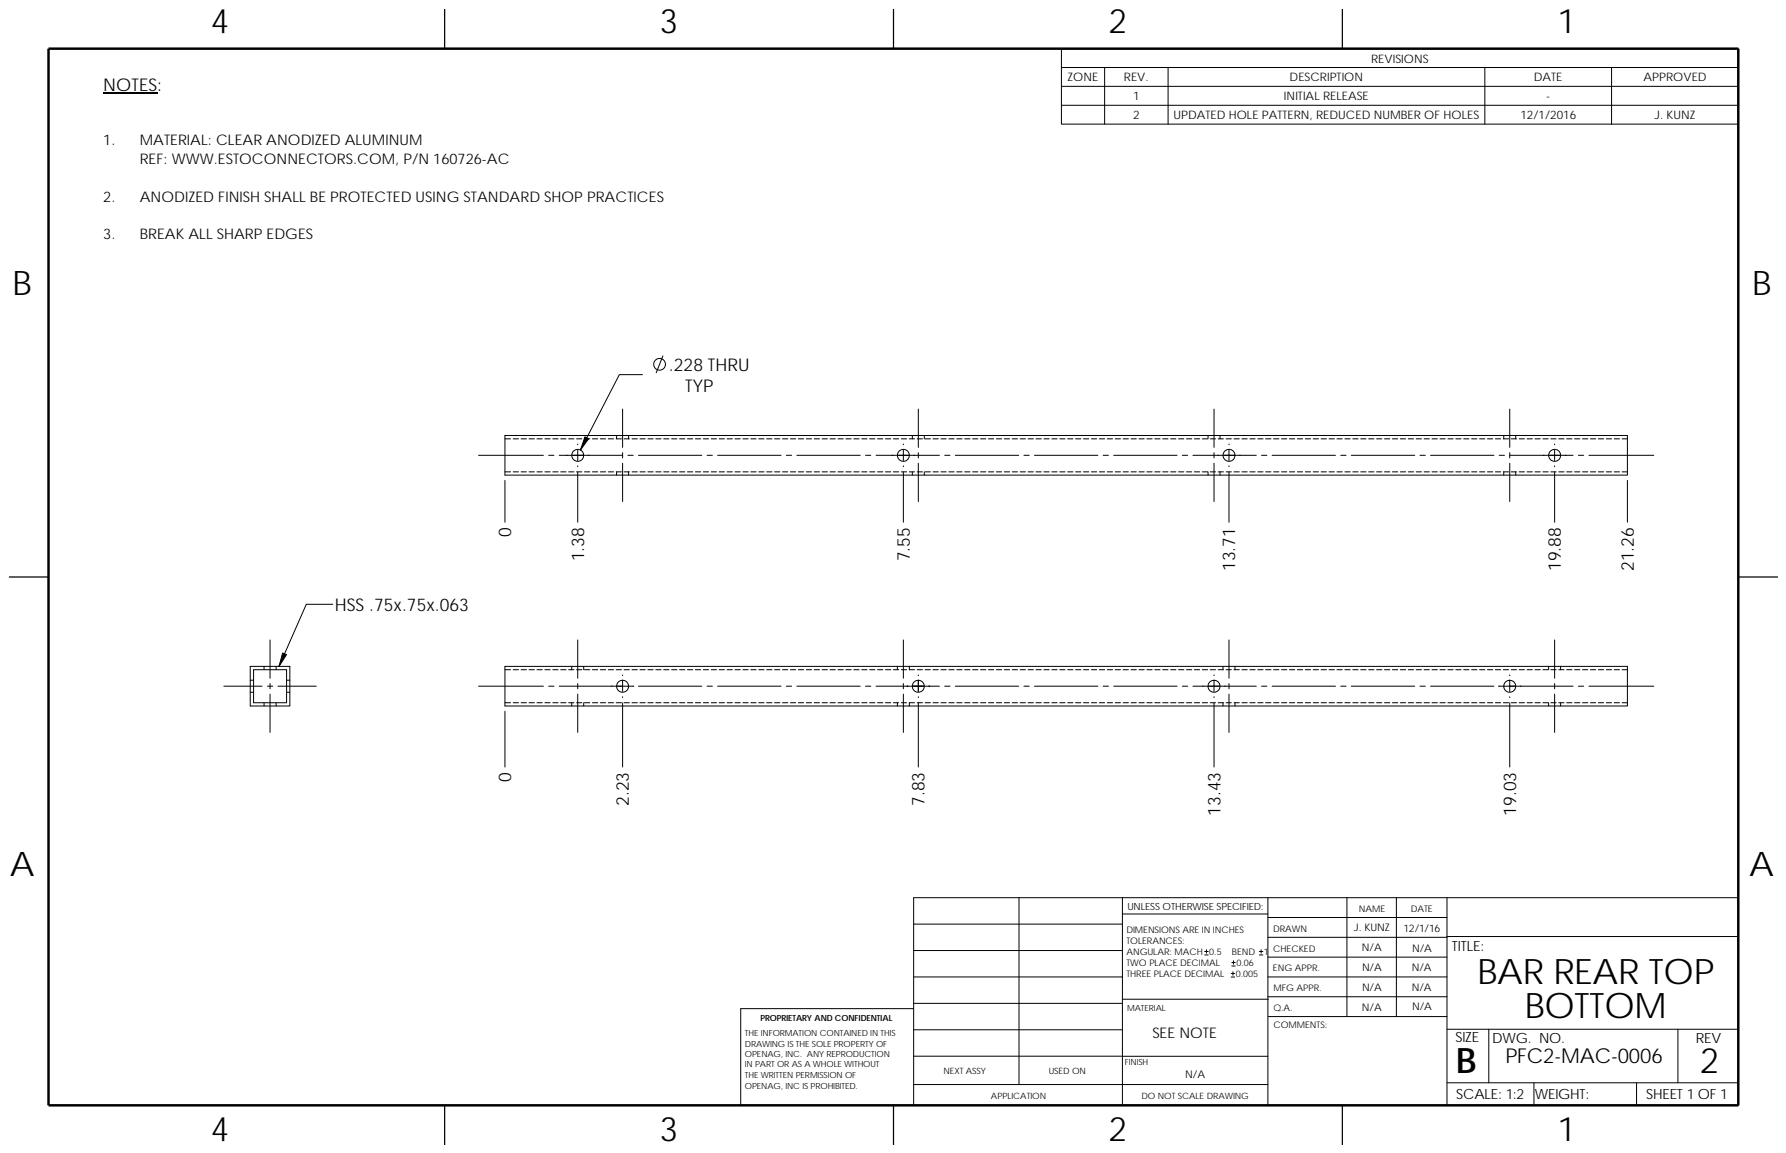
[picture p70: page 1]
INITIAL RELEASE; UPDATED HOLE PATTERN, REDUCED NUMBER OF HOLES; J. KUNZ; NOTES:; .228 THRU TYP; APPLICATION; OPENAG, INC IS PROHIBITED.; SHEET 1 OF 1; SCALE: 1:2; WEIGHT:; COMMENTS:; HSS .75x.75x.063

1. MATERIAL: CLEAR ANODIZED ALUMINUM
REF: WWW.ESTOCONNECTORS.COM, P/N 160726-AC

2. ANODIZED FINISH SHALL BE PROTECTED USING STANDARD SHOP PRACTICES

3. BREAK ALL SHARP EDGES

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

CHECKED | N/A | N/A | TITLE: BOTTOM
ENG APPR. | | N/A | BAR REAR TOP N/A N/A

MFG APPR. | | N/A

MATERIAL SEE NOTE | Q.A. | N/A | N/A

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

NEXT ASSY | USED ON | SIZE B | DWG. NO. | REV 2 PFC2-MAC-0006

FINISH N/A

DO NOT SCALE DRAWING

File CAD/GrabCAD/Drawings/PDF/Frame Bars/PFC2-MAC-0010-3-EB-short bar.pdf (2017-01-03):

2

4 | 3 | 1

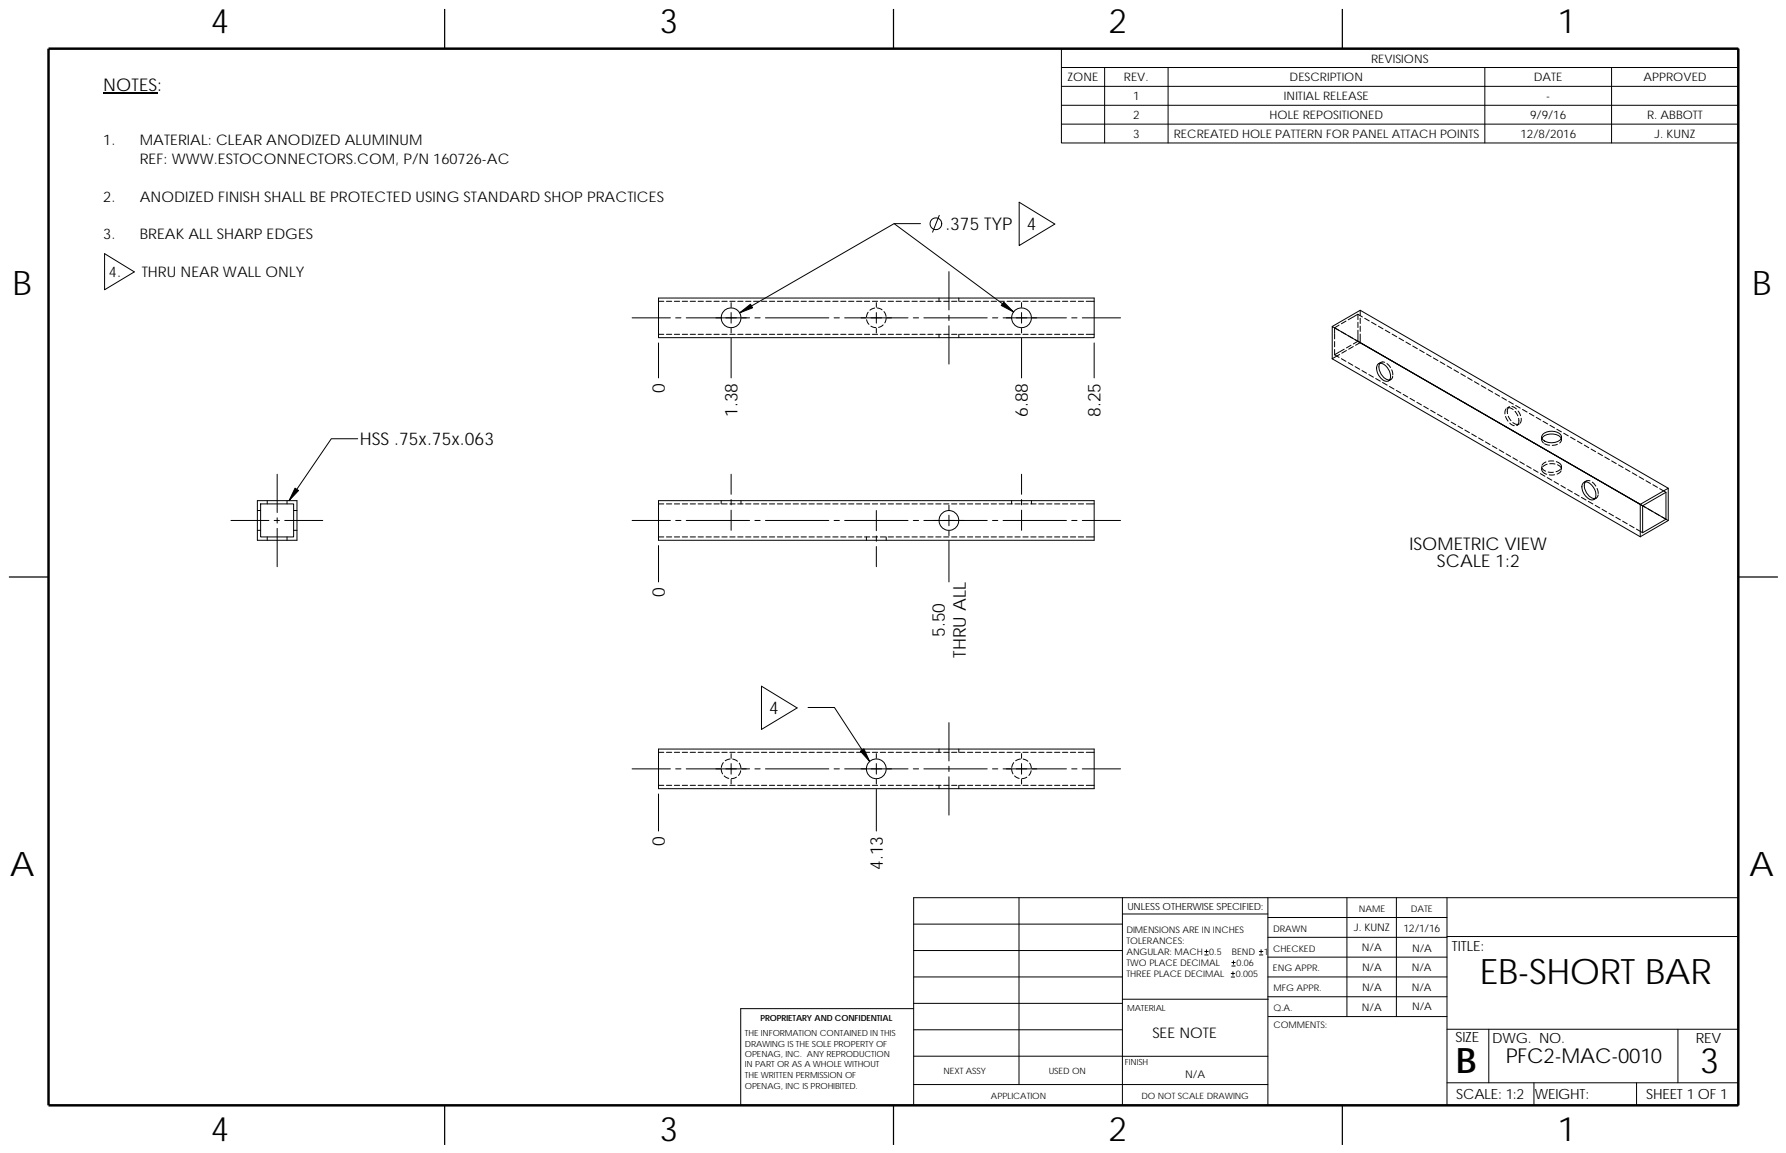
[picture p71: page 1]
THRU ALL; HSS .75x.75x.063; OPENAG, INC IS PROHIBITED.; SHEET 1 OF 1; WEIGHT:; SCALE: 1:2; COMMENTS:; APPLICATION; REVISIONS; ZONE; REV.; DESCRIPTION; DATE; APPROVED; INITIAL RELEASE; HOLE REPOSITIONED; R. ABBOTT; RECREATED HOLE PATTERN FOR PANEL ATTACH POINTS; J. KUNZ; NOTES:; ISOMETRIC VIEW SCALE 1:2; .375 TYP 4

1. MATERIAL: CLEAR ANODIZED ALUMINUM
REF: WWW.ESTOCONNECTORS.COM, P/N 160726-AC

2. ANODIZED FINISH SHALL BE PROTECTED USING STANDARD SHOP PRACTICES

3. BREAK ALL SHARP EDGES

4. THRU NEAR WALL ONLY

UNLESS OTHERWISE SPECIFIED: | | NAME | DATE
DIMENSIONS ARE IN INCHES TOLERANCES: ANGULAR: MACH 0.5 BEND 1 TWO PLACE DECIMAL 0.06 THREE PLACE DECIMAL 0.005 | DRAWN | J. KUNZ | 12/1/16
CHECKED | N/A | N/A | TITLE: EB-SHORT BAR

ENG APPR. | N/A | N/A
MFG APPR. | N/A | N/A

MATERIAL SEE NOTE | Q.A. | N/A | N/A

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

SIZE B | DWG. NO. PFC2-MAC-0010 | REV 3

NEXT ASSY | USED ON | FINISH N/A

DO NOT SCALE DRAWING

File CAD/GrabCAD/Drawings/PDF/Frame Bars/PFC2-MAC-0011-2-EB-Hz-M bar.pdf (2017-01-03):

4 | 2 | 1
3

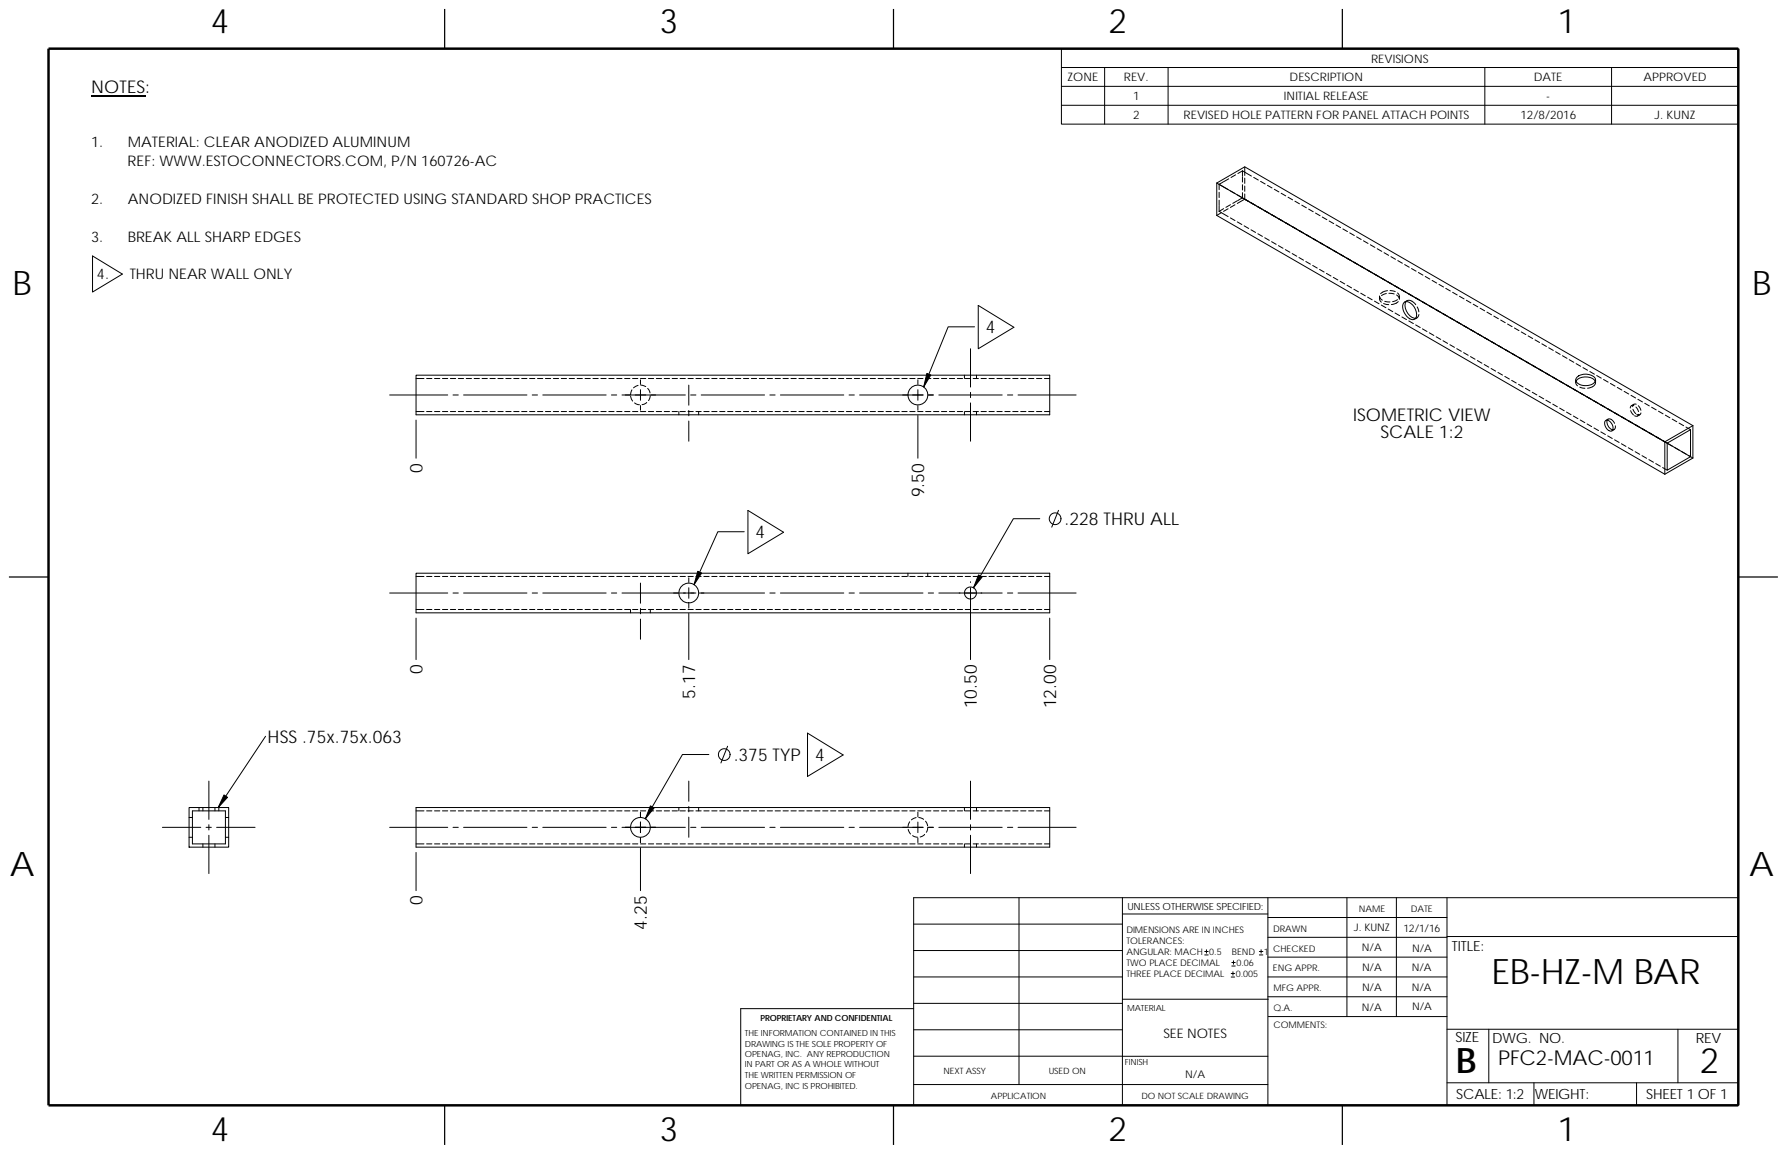
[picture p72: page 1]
4.25 J. KUNZ; COMMENTS:; REVISIONS; ZONE; REV.; DESCRIPTION; DATE; APPROVED; INITIAL RELEASE; REVISED HOLE PATTERN FOR PANEL ATTACH POINTS; J. KUNZ; NOTES:; .228 THRU ALL; .375 TYP 4; HSS .75x.75x.063; ISOMETRIC VIEW SCALE 1:2

1. MATERIAL: CLEAR ANODIZED ALUMINUM
REF: WWW.ESTOCONNECTORS.COM, P/N 160726-AC

2. ANODIZED FINISH SHALL BE PROTECTED USING STANDARD SHOP PRACTICES

3. BREAK ALL SHARP EDGES

4. THRU NEAR WALL ONLY

UNLESS OTHERWISE SPECIFIED: | | NAME | DATE

DIMENSIONS ARE IN INCHES TOLERANCES: ANGULAR: MACH 0.5 BEND 1 TWO PLACE DECIMAL 0.06 THREE PLACE DECIMAL 0.005 | DRAWN | | 12/1/16

CHECKED | N/A | N/A | TITLE: EB-HZ-M BAR
ENG APPR. | N/A | N/A
MFG APPR. | N/A | N/A

MATERIAL SEE NOTES | Q.A. | N/A | N/A

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

SIZE B | DWG. NO. PFC2-MAC-0011 | REV 2

NEXT ASSY | USED ON | FINISH N/A

APPLICATION | DO NOT SCALE DRAWING | | SCALE: 1:2 | WEIGHT: | SHEET 1 OF 1

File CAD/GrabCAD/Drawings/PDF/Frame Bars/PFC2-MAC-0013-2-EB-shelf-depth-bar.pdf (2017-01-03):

4 | 3 | 2 | 1

## REVISIONS

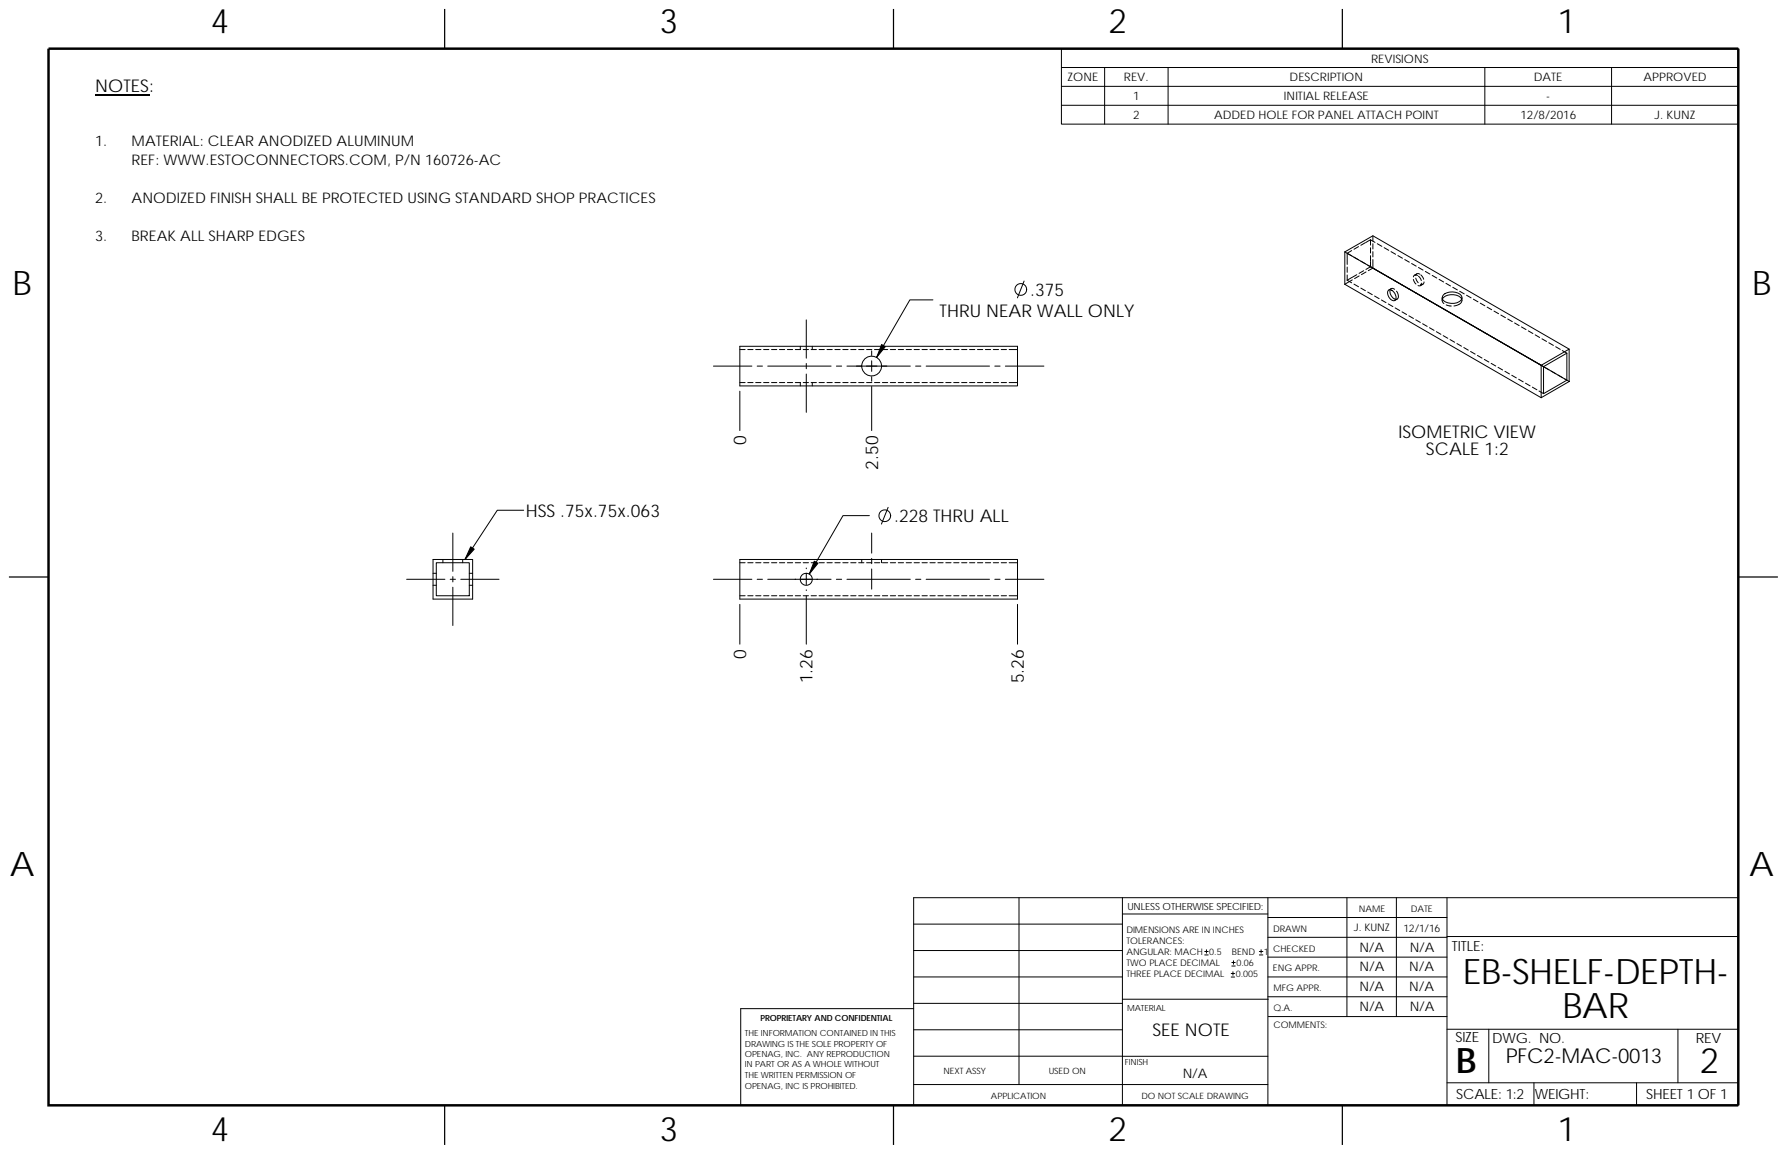
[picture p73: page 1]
.228 THRU ALL; SHEET 1 OF 1; SCALE: 1:2; WEIGHT:; COMMENTS:; ZONE; REV.; DESCRIPTION; DATE; APPROVED; INITIAL RELEASE; ADDED HOLE FOR PANEL ATTACH POINT; J. KUNZ; NOTES:; HSS .75x.75x.063; ISOMETRIC VIEW SCALE 1:2

1. MATERIAL: CLEAR ANODIZED ALUMINUM
REF: WWW.ESTOCONNECTORS.COM, P/N 160726-AC

2. ANODIZED FINISH SHALL BE PROTECTED USING STANDARD SHOP PRACTICES

3. BREAK ALL SHARP EDGES

THRU NEAR WALL ONLY

UNLESS OTHERWISE SPECIFIED: | | NAME | DATE
DIMENSIONS ARE IN INCHES TOLERANCES: ANGULAR: MACH 0.5 BEND 1 TWO PLACE DECIMAL | DRAWN | J. KUNZ | 12/1/16

CHECKED | N/A | N/A | TITLE: EB-SHELF-DEPTH-BAR
ENG APPR. | N/A | N/A
MFG APPR. | N/A | N/A

NEXT ASSY APPLICATION | 0.06 THREE PLACE DECIMAL 0.005 USED ON PROPRIETARY AND CONFIDENTIAL

MATERIAL SEE NOTE | Q.A. | N/A | N/A

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

SIZE B | DWG. NO. PFC2-MAC-0013 | REV 2

FINISH N/A

DO NOT SCALE DRAWING

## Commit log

2016-11-03 Initial upload of the Solidworks CAD model
    [1-bar-frame.SLDASM, 1-bar-frame.SLDDRW, 10-24_075_spacer.SLDPRT, 10-24_screw01.SLDPRT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]
2017-01-03 Full New Model
    [1-bar-frame.SLDASM, 1-bar-frame.SLDDRW, 10-24_075_spacer.SLDPRT, 10-24_screw01.SLDPRT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]
2017-01-03 Additions: DXF files, isulation, Drawings
    Upload Includes: DXF files for Acrylic, foam, and insulation. Drawings
    for Frame bars, sheet metal parts, and acrylic panels.
    [1-bar-frame.SLDDRW, Accesory Plate.DXF, Assem1cam.SLDASM, Chiller base plate.DXF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]
2017-01-06 Added Ordering BOM
    See BOM-MASTER
    [BOM-MASTER.xlsx]
2017-01-06 Now sorting by distributor for easy ordering
    [BOM-MASTER.xlsx]
2017-01-11 Frame instruction editing
2017-01-11 edits and rewrites
    edits and rewrites of frame section
2017-01-24 Sub-assembly BOM details; other links
2017-02-08 Correct number of connectors on the Base Layer
    We only need 2 of CON-0002 instead of 3.
2017-02-08 Organize File Naming Conventions
    [1-bar-frame.SLDDRW, 12-6-6-Box.sldprt, 120mm_fan.SLDPRT, 12V-PS-SE-450-12.SLDPRT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]
2017-02-10 Split Instructions by Submodule
    [BOM_MASTER.xlsx, BOM_Sub_Assemblys.xlsx]
2017-02-10 Continue Reorganizing Documentation
    [Accesory Plate.DXF, Chiller base plate.DXF, EB-panel-front.DXF, EB-panel-rear.DXF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]
2017-02-10 Sort the FAS-PCK-0001 by baggie number
    [BOM_MASTER.xlsx]
2017-02-12 Add "Bag Number" to all instructions
    [BOM_MASTER.xlsx, BOM_Sub_Assemblys.xlsx]
2017-03-26 Fixing link to the Bill of Materials
    Link to the Bill of Materials pointed to a 404. Updated it to point to the correct address.
    Changed from "../BOM/BOM_Master.xls" to "./BOM/BOM_MASTER.xls"
